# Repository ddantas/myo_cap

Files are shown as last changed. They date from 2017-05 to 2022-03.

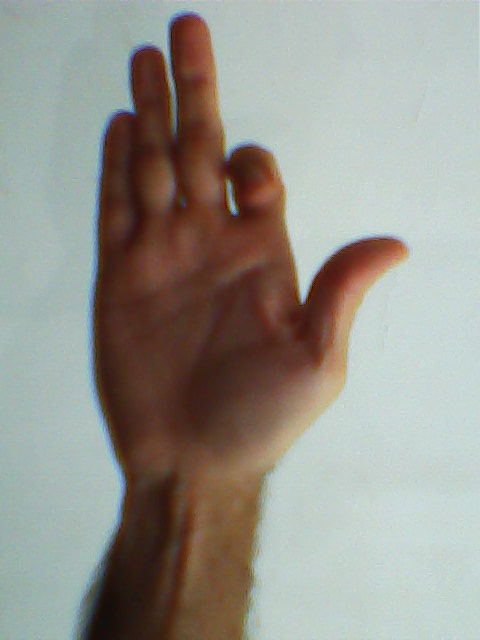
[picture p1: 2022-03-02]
software/interface/leap_cap/images/2in_curl.jpg

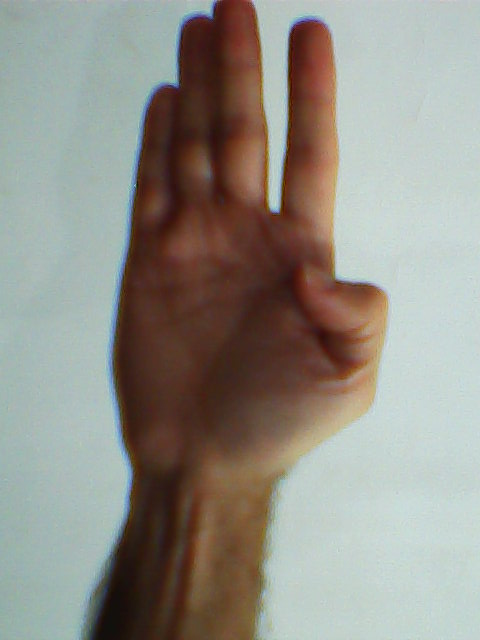
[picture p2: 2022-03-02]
software/interface/leap_cap/images/1th_curl.jpg

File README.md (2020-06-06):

# myo_cap #

## Boas práticas ##
- Antes de começar a trabalhar no código, para baixar as modificações dos outros programadores, sempre chame:
```
git pull
```

- Antes de dar commit, para ver quais arquivos foram modificados, usar:
```
git status
```

- Em seguida, apenas para os arquivos que precisam realmente ser enviados no commit, dar:
```
git add nome_do_arquivo
```

- Ao dar commit, é recomendável usar:
```
git commit -m "mensagem em inglês com o nome do commit"
```

- Depois disso, para fazer o merge com possíveis alterações recentes, dar
```
git pull
```

- E, finalmente:
```
git push
```

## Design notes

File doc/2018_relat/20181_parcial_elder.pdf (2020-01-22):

## UNIVERSIDADE FEDERAL DE SERGIPE CENTRO DE CIÊNCIAS EXATAS E TECNOLOGIA

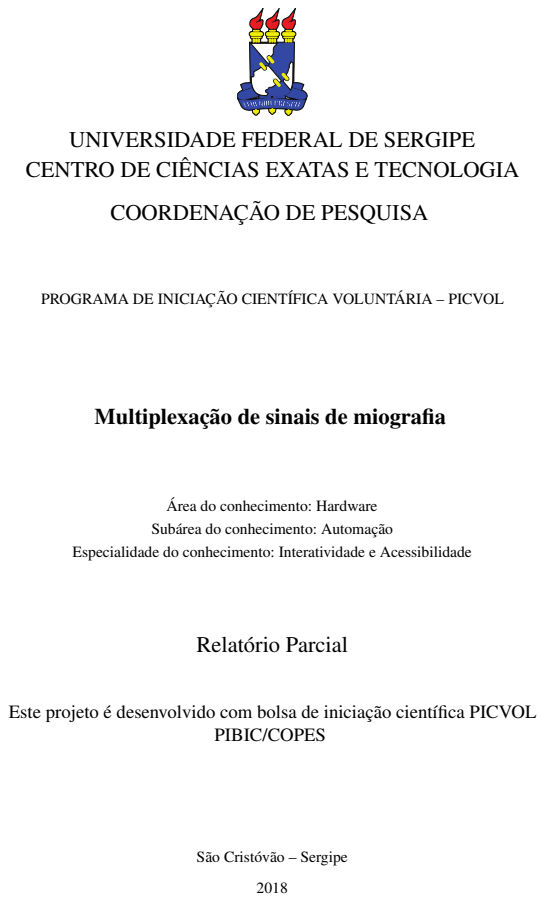
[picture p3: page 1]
Relatório Parcial; PIBIC/COPES

COORDENAÇÃO DE PESQUISA

PROGRAMA DE INICIAÇÃO CIENTÍFICA VOLUNTÁRIA – PICVOL

Multiplexação de sinais de miografia

Área do conhecimento: Hardware

Subárea do conhecimento: Automação

Especialidade do conhecimento: Interatividade e Acessibilidade

Este projeto é desenvolvido com bolsa de iniciação científica PICVOL

São Cristóvão – Sergipe

# Sumário

1

# Atividades Realizadas

Inicialmente, foi feita a revisão bibliográfica a respeito das aplicações e uso dos circuitos multiplexadores no campo dos biosinais podendo ser: eletrocardiograma, eletro-oculograma e eletromiografia.

Após a revisão bibliográfica, foi feita a pesquisa sobre qual o multiplexador atenderia aos requisitos para trabalhar com sinal mioelétrico, que possui baixa amplitude e baixa frequência.

Segundo Wang (2016), o multiplexador deve possuir baixa resistência de ligação (Ron) e baixa distorção no chaveamento dos canais, então atendendo a estes requisitos foi escolhido o multiplexador analógico CD4051.

Logo em seguida foi projetado os circuitos de multiplexação, de modo que fossem utilizados componentes de baixo custo e de fácil aquisição, comercialmente. Para isto foi utilizado o software Protheus.

Com os componentes em mãos foi feita a montagem do circuito de multiplexação para quatro canais em uma protoboard. Esse circuito tem como objetivo multiplexar os sinais obtidos de várias placas de 4 canais. Possibilitando trabalhar com um número maior de canais.

E por fim, o circuito foi testado com o auxílio do gerador de sinais e o osciloscópio, a fim de verificar a funcionalidade da comutação entre canais. Para que possa ser confeccionada a placa de circuito impresso – PCB.

2

# Justificativas de Alteração no Plano de Tra-

# balho

Não se aplica.

3

# Outras Atividades

- Participei da atividade de extensão: Seminários Sobre Internet das Coisas – IOT, com carga horária de 3 horas, coordenado pelo professor Antonio Ramirez Hidalgo, promovido pelo Departamento de Engenharia Elétrica. Onde um dos temas abortados, com relevância a esta pesquisa, foi o Monitoramento Cardíaco via Internet das Coisas. A atividade foi realizada no período de 29 a 31 de agosto de 2017;
- Participei da atividade de extensão: Electrical Day 2017, com carga horária de 8 horas, promovido pelo Empresa Júnior de Engenharia Elétrica – EPJEL, no mini curso de impressão 3D, que pode contribui no contexto geral desta pesquisa na confecção de uma mão robótica. A atividade foi realizada no dia 18 de novembro de 2017;
- Participei da atividade de extensão: IV SEMAC - minicursos Pibic 2017, com carga horária de 8 horas, coordenada pela Professora Raquel Simoes Mendes Netto, promovida pela coordenação de pesquisa, no minicurso Redação Científica e Plágio Acadêmico. A atividade foi realizada no período de 20 a 24 de novembro de 2017.
- Também foi produzido um artigo para submissão no IEEE Symposium on Computers and Communications – ISCC com qualis A2, que ocorrerá em Junho de 2018, na cidade de Natal. O título do artigo é Low cost hardware and software platform for multichannel surface electromyography. A submissão foi realizada no mês de Janeiro e em Março é esperado o resultado de aceitação.

4

# Revisão da Literatura

Eletromiografia é uma área que lida com a detecção, análise e o uso do sinal elétrico que emana das contrações musculares. Este sinal pode ser usado em diversas aplicações, desde o monitoramento dos músculos, em reabilitação de pessoas que perderam movimentos, em esportes para verificar a fadiga dos músculos e até mesmo controle de próteses biônicas (LUCA, 2006).

Amputados e indivíduos parcialmente paralisados tipicamente tem músculos intactos podendo exercer graus de liberdade variados de controle sobre estes. Além disso, existem evidências de que amputados que perderam a mão são capazes de gerar sinais nos músculos do antebraço muito semelhantes ao de uma pessoa saudável (ERIKSSON; SEBELIUS; BALKENIUS, 1998).

Para certas aplicações, como o controle de mão robótica é necessário um número maior de canais que possibilite uma quantidade maior de informações, a fim de controlar com precisão os movimentos de flexão dos dedos, do pulso ou da mão. Então é necessário multiplexar os sinais para reduzir o número de dados de saída.

Um multiplexador é um dispositivo que seleciona uma saída de muitas entradas em uma base de seleção linear e é uma parte fundamental das aplicações biomédicas (D et al., 2013).

Este plano de trabalho tem como objetivo utilizar um circuito multiplexador na etapa intermediaria entre aquisição e conversão analógico digital do sinal mioelétrico. O que permite reduzir os custos quando se deseja trabalhar com diversos canais.

5

# Metodologia

Na figura 1 é mostrado o diagrama de blocos do sistema de aquisição, multiplexação e digitalização do sinal mioelétrico. Que é composto por até 4 placas de aquisição, circuito de multiplexação, placa Tiva e um computador para visualizar os diversos sinais mioelétricos adquiridos. A etapa de multiplexação é opcional, utilizada em aplicações que necessitem de uma quantidade maior de canais.

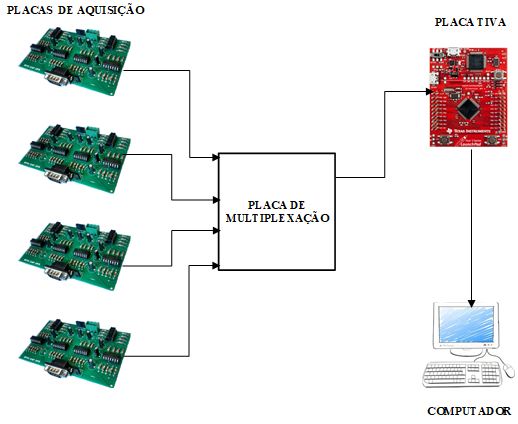
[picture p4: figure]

Figura 1 – Diagrama de blocos da plataforma.

Capítulo 5. Metodologia | 7

Na figura 2 é mostrado o diagrama esquemático da placa de multiplexação, nesse circuito é possível conectar 4 placas de aquisição de 4 canais, o total de canais que podem ser capturados com está placa são 16. A seguir é listada a nomenclatura de cada terminal:

- BOARD X – conector onde é ligado cada placa de aquisição e condicionamento do sinal mioelétrico, onde o X varia de 1 a 4;
- SELECT CHANNEL – terminais que serão ligados aos pinos da Tiva e servem para realizar a seleção de canais que serão habilitados na saída do mux;
- OUT MUX – saída dos multiplexadores que serão ligados a um circuito somador;
- TO TIVA – saída do circuito somador que será ligada a placa Tiva;
- POWER – alimentação simétrica de -9 e +9V.

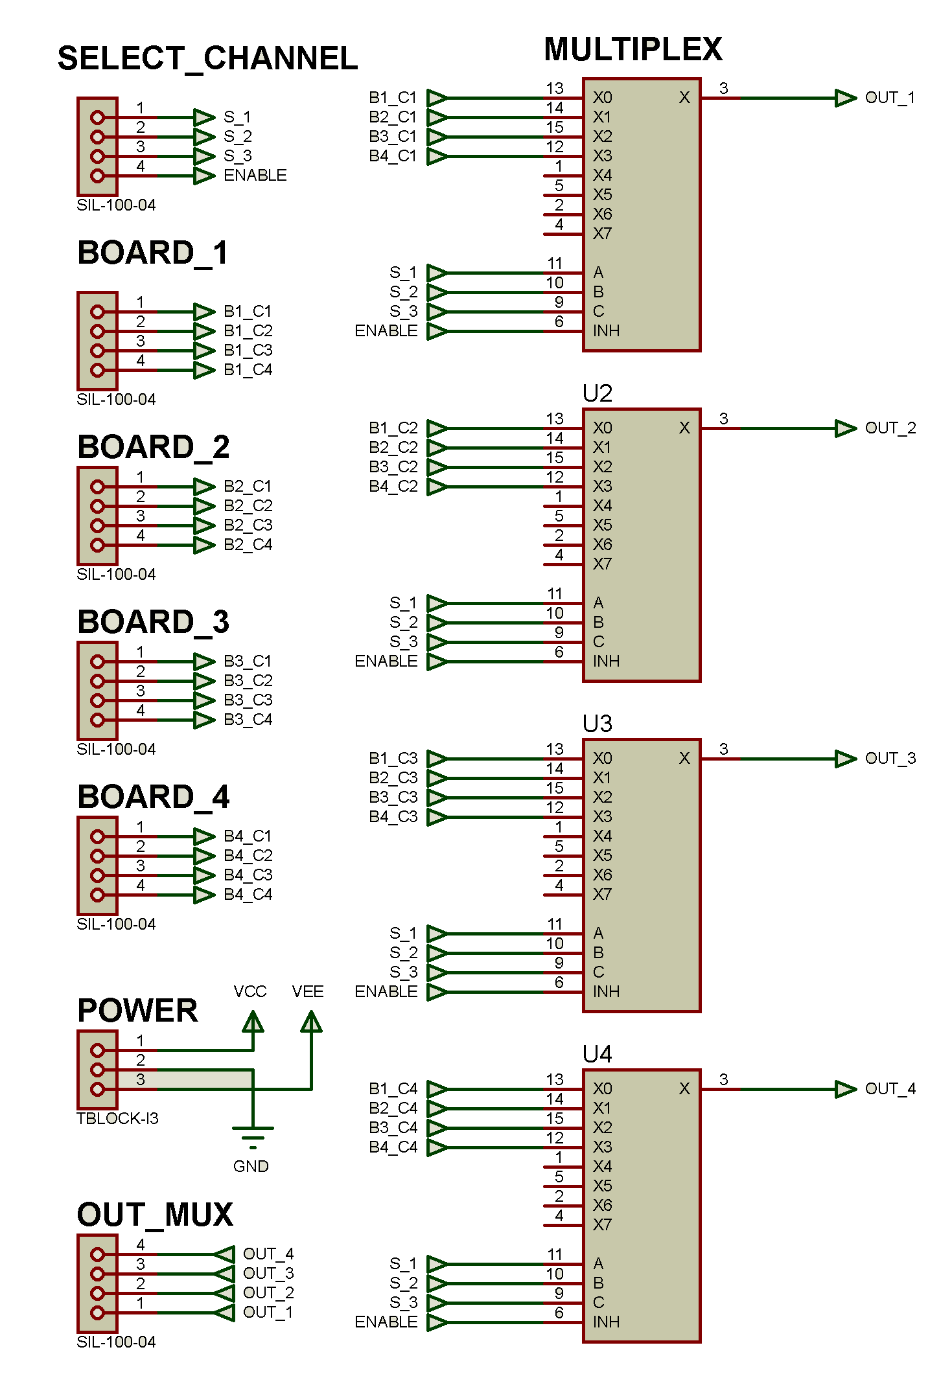
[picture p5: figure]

Figura 2 – Diagrama esquemático do circuito de multiplexação para canais.

Capítulo 5. Metodologia | 8

O multiplexador e demultiplexador analógico CD 4051 de 8 canais é um circuito integrado com tecnologia complementary metal-oxide-semiconductor – CMOS que possui 16 pinos, sendo 3 pinos de endereçamento (S1 a S3), 8 pinos independentes de entradas/saídas – I/O (Y0 a Y7) conectados a um pino comum I/O (Z). A tensão de alimentação é de 3 a 15V (VEE, VSS e VDD) e a tensão de operação é de 0 a 2 para nível logico baixo e 2.1 a 5 para nível logico alto (NEXPERIA, 2016). Na figura 3 é mostrado este circuito integrado.

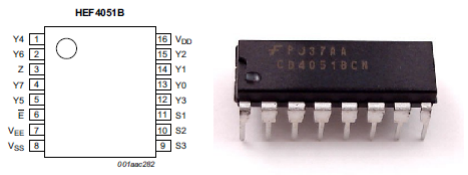
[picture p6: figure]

Figura 3 – Circuito integrado CD4051.

Neste trabalho foi utilizado a placa de desenvolvimento Tiva-C series EK-TM4C123GXL, responsável por realizar a conversão analógico-digital do sinal mioelétrico e a seleção dos canais das placas conectadas ao multiplexador a uma dada frequência de chaveamento.

É uma plataforma de baixo custo que possui microcontrolador ARM Cortex M4 de 32

bits operando a 80 MHz. Este microcontrolador é encontrados em telefones celulares, calculadoras, periféricos de computadores, equipamentos eletrônicos em geral e aplicações industriais (SOUZA, ). Na figura 4 é mostrado a placa de desenvolvimento Tiva, para programá-la pode ser usado a linguagem C com compilador fornecido pela Texas Instruments Code Composer Studio – CCS.

A placa tiva opera com valores positivos de tensão em suas entradas conectadas ao seu conversor analógico-digital, então foi necessário utilizar um circuito que eleve o nível de tensão (off-set) em 1.6V após a etapa de multiplexação, pois o sinal mioelétrico é de natureza analógica tendo valores negativos e positivos de tensão. Este circuito somador de tensão é apresentado na figura 5 abaixo.

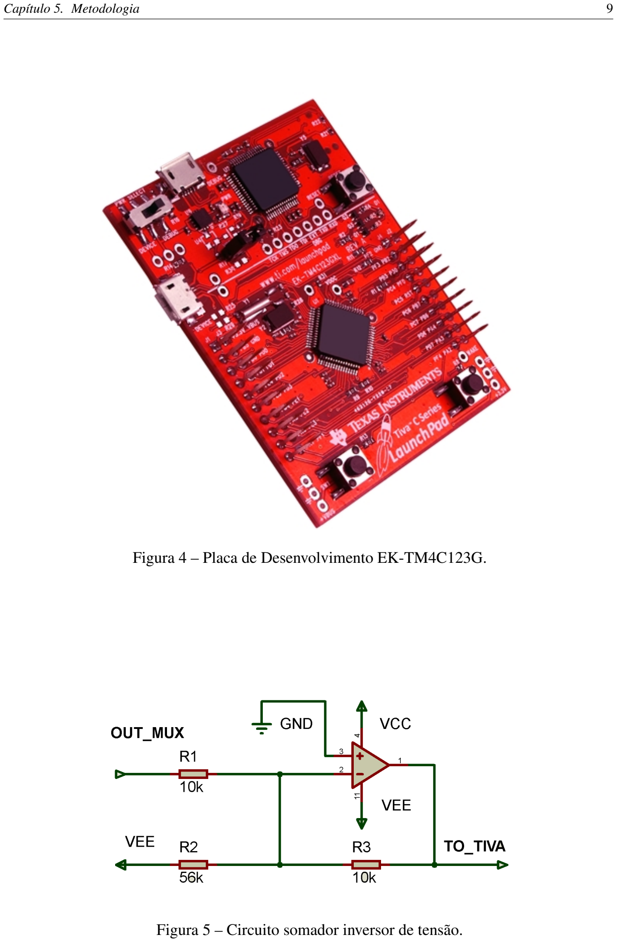
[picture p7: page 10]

Capítulo 5. Metodologia | 9

Figura 4 – Placa de Desenvolvimento EK-TM4C123G.

Figura 5 – Circuito somador inversor de tensão.

6

# Resultados preliminares

O circuito de multiplexação para quatro canais foi montado em uma protoboard em conjunto com o circuito somador e podem ser vistos na figura 6. Este circuito foi testado utilizando gerador de sinais e osciloscópio.

Foram utilizados dois sinais de entrada através do gerador de funções foi possível obter uma onda senoidal e outra onda quadrada com frequência e amplitude aproximadamente iguais como pode ser visto na figura 7

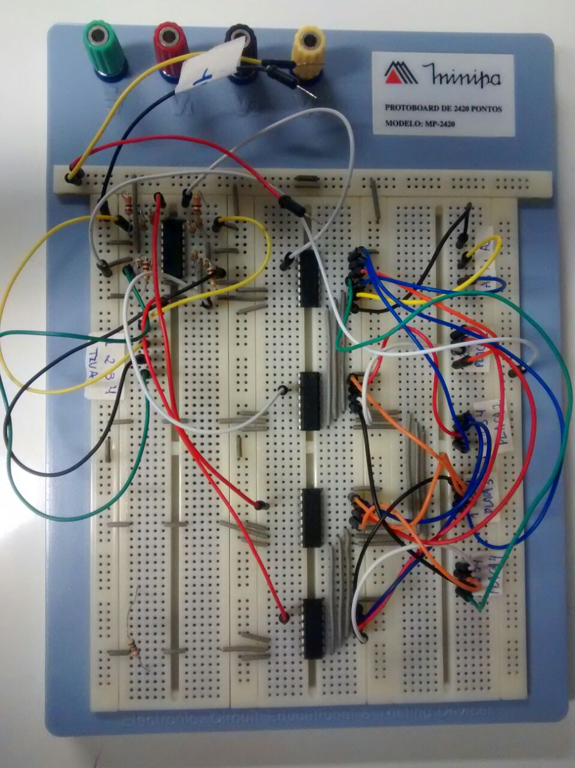
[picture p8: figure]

Figura 6 – Circuito de multiplexação montado na protoboard.

Capítulo 6. Resultados preliminares | 11

Estes sinais foram conectados a duas entradas do circuito multiplexador e a saída pode ser observada nas figuras 8 e 9. Os dois sinais de entrada simulam dois canais da placa de aquisição e na saída teremos a composição de ambos os sinais. A frequência de chaveamento e a frequência dos sinais de entrada foram variadas entre a frequência mínima e máxima do sinal mioelétrico que pela literatura é de 20 a 500Hz (LUCA, 2006).

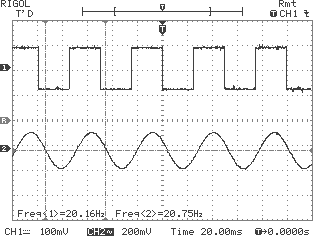
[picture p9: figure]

Figura 7 – Tela de captura do osciloscópio do sinais de entrada (onda senoidal e quadrada).

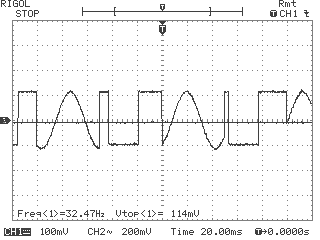
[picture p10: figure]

Figura 8 – Tela de captura do osciloscópio saída com frequência de 20Hz.

Capítulo 6. Resultados preliminares | 12

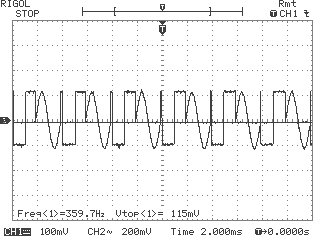
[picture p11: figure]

Figura 9 – Tela de captura do osciloscópio saída com frequência de 500Hz.

O sinal de saída é composto por um ciclos de onda quadrada e um ciclo de onda senoidal, como podem ser observados nas figuras 8 e 9. Estes sinais não sofreram distorções no chaveamento para a menor e a maior frequência do sinal aplicado.

Portanto o resultado preliminar, encontra-se dentro do esperado. Como trabalho futuro espera-se confeccionar este circuito de multiplexação em uma placa de circuito impresso e aumentar a quantidade de canais para oito.

# Referências

D, H. P. et al. Design of Ultra Low Power 8-Channel Analog Multiplexer Using Dynamic Threshold for Biosignals. [S.l.: s.n.], 2013. v. 4. DOI: 10.5121/vlsic.2013.4508.

ERIKSSON, L.; SEBELIUS, F.; BALKENIUS, C. Neural Control of a Virtual Prosthesis. In: TAYLOR, J. G. et al. (Ed.). ICANN 98. London: Springer London, 1998. p. 905–910. ISBN 978-3-540-76263-8 978-1-4471-1599-1. DOI: 10.1007/978-1-4471-1599-1_141. Disponível em: <http://link.springer.com/10.1007/978-1-4471-1599-1_141>.

LUCA, C. D. Electromyography. In: Encyclopedia of Medical Devices and Instrumentation. John Wiley & Sons, Inc., 2006. ISBN 978-0-471-73287-7. DOI: 10.1002/0471732877.emd097. Disponível em: <http://onlinelibrary.wiley.com/doi/10.1002/0471732877.emd097/abstract>.

NEXPERIA. HEF4051B 8-Channel Analog Multiplexer/Demultiplexer Datasheet. 2016. Disponível em: <https://assets.nexperia.com/documents/data-sheet/HEF4051B.pdf>.

SOUZA, S. A. Introdução aos microcontroladores ARM Cortex-M4 Tiva C Series da Texas Instruments. Disponível em: <http://www.ebah.com.br/content/ABAAAgv0gAJ/introducao-aos-microcontroladores-arm-cortex-m4-tiva-c-series-texas-instruments>. (http://www.ebah.com.br/content/ABAAAgv0gAJ/introducao-aos-microcontroladores-arm-cortex-m4-tiva-c-series-texas-instruments)

WANG, R. A Low Power 8 to 1 Analog Multiplexer for Bio-Signal Acquisition System with a Function of Amplification. Tese (Text) — Carleton University, 2016. Disponível em: <https://curve.carleton.ca/88679474-7bcd-436e-8551-e62864841f7a>.

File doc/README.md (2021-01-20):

# Link para requisitos de software #

https://www.dropbox.com/s/pmltx1t9zvk2afu/myo_cap_gui_requisitos_2021.pdf?dl=0

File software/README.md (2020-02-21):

# Funções Tivaware #

## 1.	Clock Geral do Sistema ##

### SyzCtlClockSet(uint32_t ui32Config) ###
- <b>Definição</b>: Configuração do clock geral do sistema. 
- <b>Parâmetros</b>: “ui32Config” é o parâmetro, ou os parâmetros de configuração (quando vários parâmetros, os mesmos são separados por “|”).
- <b>Exemplo</b>: 
```
SysCtlClockSet(SYSCTL_SYSDIV_5|SYSCTL_USE_PLL|SYSCTL_XTAL_16MHZ|SYSCTL_OSC_MAIN);
```
No exemplo acima, pode ser verificado a utilização de um cristal externo de 16MHz, representados pelos parâmetros SYSCTL_XTAL_16MHZ e SYSCTL_OSC_MAIN e configuração do clock do sistema através de uma PLL (que possui 200MHz de referencia para cálculos) e divisão da mesma por 5, representadas pelos parâmetros SYSCTL_SYSDIV5 e SYSCTL_USE_PLL. 
Assim, o clock geral do sistema estará configurado para trabalhar com o cristal de 16 MHz da placa de desenvolvimento e estará funcionando a 40 MHz conforme a divisão da PLL escolhida.

### SysCtlPeripheralEnable(ui32Peripheral) ###
- <b>Definição</b>: Função para habilitar periférico, como o GPIO.
- <b>Parâmetros</b>: “ui32Peripheral” é o periférico a ser habilitado.
- <b>Exemplo</b>: 
```
SysCtlPeripheralEnable(SYSCTL_PERIPH_GPIOF);
```
Habilitação do periférico GPIO Port F.

## 2.	Configurando e usando o GPIO ##
### GPIOPinTypeGPIOOutput(uint32_t ui32Port, uint8_t ui8Pins) ###
- <b>Definição:</b> Função onde um pino da GPIO é configurado como saída.
- <b>Parâmetros:</b> “ui32Port” representa o PORT a ser configurado e o “ui8Pins” o pino.

### GPIOPinTypeGPIOInput(uint32_t ui32Port, uint8_t ui8Pins) ###
- <b>Definição:</b> Função onde um pino da GPIO é configurado como entrada.
- <b>Parâmetros:</b> “ui32Port” representa o PORT a ser configurado e o “ui8Pins” o pino.
- <b>Exemplo</b>:
```
  SysCtlPeripheralEnable(SYSCTL_PERIPH_GPIOF); 
  GPIOPinTypeGPIOOutput(GPIO_PORTF_BASE, GPIO_PIN_1|GPIO_PIN_2|GPIO_PIN_3);
  GPIOPinTypeGPIOInput(GPIO_PORTF_BASE, GPIO_PIN_4|GPIO_PIN_0);
```
O exemplo acima configura na PORT F, os pinos PF1, PF2 e PF3 como saída (LED RGB da Launchpad) e os pinos PF0 e PF4 como entrada (dois botões da Launchpad). 

### GPIOPinRead(uint32_t ui32Port, uint8_t ui8Pins) ###
- <b>Definição:</b> Função que retorna se o pino está em nível lógico alto ou baixo.
- <b>Parâmetros: </b> “ui32Port” representa o PORT e o “ui8Pins” o pino a serem lidos.
- <b>Exemplo:</b> 
```
GPIOPinRead(GPIO_PORTF_BASE, GPIO_PIN_4);
```
Retorna o endereço, ou valor, do PIN_4 do PORTF caso 1.

### GPIOPinWrite(uint32_t ui32Port, uint8_t ui8Pins, uint8_t ui8Val) ###
- <b>Definição:</b> Função que manda o nível lógico alto ou baixo para o pino em questão.
- <b>Parâmetros:</b> “ui32Port” representa o PORT, o “ui8Pins” o pino de entrada e “ui8Val” o valor.
- <b>Exemplo:</b> 
```
GPIOPinWrite(GPIO_PORTF_BASE,GPIO_PIN_1|GPIO_PIN_2|GPIO_PIN_3,GPIO_PIN _2); 
```
Aciona somente o PIN_2 do PORTF

## 3.	Utilizando uma UART ##

### UARTConfigSetExpClk(uint32_t ui32Base, uint32t ui32UARTClk, uint32_t ui32Baud, uint32_t ui32Config) ###
- <b>Definição:</b> Função que configura os parâmetros da serial utilizada.
- <b>Parâmetros:</b> “ui32Base” é a UART port ,  “ui32UARTClk” é o clock disponível para o modulo UART, “ui32Baud” é o baud rate, “ui32Config” indica o formato dos dados.

### UARTCharPut(uint32_t ui32Base, unsigned char ucData) ###
- <b>Definição: </b> Função que imprime na serial o parâmetro ucData.
- <b>Parâmetros: </b> “ui32Base” é a UART port, “ucData” é o caractere a ser transmitido.

### UARTPrintf(unsigned char *ucData) ###
- <b>Definição: </b> Função que imprime na serial o parâmetro ucData.
- <b>Parâmetros: </b> “ucData” é o caractere a ser transmitido.

### UARTCharGet(uint32_t ui32Base) ###
- <b>Definição:</b> Função que retorna o caractere lido na serial como int32_t.
- <b>Parâmetros:</b> “ui32Base” é a UART port.
- <b>Exemplo:</b> 
```
void ConfigureUART(void) { 
  SysCtlPeripheralEnable(SYSCTL_PERIPH_GPIOA);
  SysCtlPeripheralEnable(SYSCTL_PERIPH_UART0);
  GPIOPinConfigure(GPIO_PA0_U0RX); 
  GPIOPinConfigure(GPIO_PA1_U0TX); 
  GPIOPinTypeUART(GPIO_PORTA_BASE, GPIO_PIN_0 | GPIO_PIN_1);
  UARTClockSourceSet(UART0_BASE, UART_CLOCK_PIOSC); 
  UARTStdioConfig(0, 115200, 16000000); 
}
```

## 4.	Configurando interrupções. ##
### Configurando o ambiente ###
- <b>1º Passo:</b> Declare a função a ser chamada através da interrupção desejada como função externa ao código, aproximadamente na linha 58 do código do “tm4c123gh6pmi_sturtup_ccs.c”.
- <b>2º Passo:</b> Adicione essa função ao vetor de interrupções em sua devida posição substituindo a função padrão “IntDefaultHandler” pela sua função utilizada. Para uma interrupção no PORTF, sua posição será aproximadamente na linha 116 do código do “tm4c123gh6pmi_startup_ccs.c”. Após estas configurações, sempre que houver uma borda de descida no pino 4 do PortF (SW1 pressionado), sua função de interrupção será executada!

### IntMasterEnable() ###
- <b>Definição:</b> Função que permite ao processador responder a todas as chamadas de interrupção utilizadas.

### GPIOIntEnable(uint32_t ui32Port, uint32_t ui32IntFlags) ###
- <b>Definição:</b> Função onde um pino da GPIO do microcontrolador é configurado como interrupção e o parâmetro ui32IntFlags representa o pino a ser configurado da seguinte forma: GPIO_INT_PIN_0, GPIO_INT_PIN_1, ... ou GPIO_INT_PIN_7.
- <b>Parâmetros:</b> “ui32Port” é o GPIO port, “ui32IntFlags” é o pino do GPIO port.

### GPIOIntTypeSet(uint32_t ui32Port, uint8_t ui8Pins, uint32_t ui32IntType) ###
- <b>Definição:</b> Função onde um pino da GPIO do microcontrolador que é configurado como interrupção tem o seu modo de habilitação configurado, e o parâmetro ui32IntType que representa o modo de habilitação da interrupção pode ser configurado como: GPIO_FALLING_EDGE (para borda de descida), GPIO_RISING_EDGE (para borda de subida), GPIO_BOTH_EDGE (qualquer borda), GPIO_LOW_LEVEL (nível lógico baixo) e GPIO_HIGH_LEVEL (nível lógico alto).
- <b>Parâmetros:</b> “ui32Port” é o GPIO port, “ui8Pins” são os pinos, “ui32IntType” representa o modo de habilitação da interrupção.

## 5.	Configurando o Timer ##

### Configurando o ambiente ###
- <b>1º Passo:</b> Declare a função a ser chamada através da interrupção desejada como função externa ao código, aproximadamente na linha 59 do código do “tm4c123gh6pmi_sturtup_ccs.c”.
- <b>2º Passo:</b> Adicione essa função ao vetor de interrupções em sua devida posição substituindo a função padrão “IntDefaultHandler” pela sua função utilizada. Para uma interrupção no PORTF, sua posição será aproximadamente na linha 106 do código do “tm4c123gh6pmi_sturtup_ccs.c”.Após estas configurações, sempre que o timer atingir o período de contagem selecionado, ele vai gerar uma interrupção e a função declarada será executada!

### TimerConfigure(uint32_t ui32Base, uint32t ui32Config) ###
- <b>Definição:</b> Função que configura o tipo de timer utilizado onde o parâmetro ui32Config e escolhido conforme a configuração de Timer periódico, Disparo único, PWM, etc.  
- <b>Parâmetros:</b> "ui32Base" é o endereço base para o modulo do timer, "ui32Config" tipo de configuração do timer (Periódico, disparo único, PWM).

### TimerEnable(uint32_t ui32Base, uint32_t ui32Timer) ###
- <b>Definição:</b> Função que habilita o timer escolhido após a sua configuração onde o parâmetro ui32Timer é o Timer escolhido: TIMER_A, TIMER_B, ou TIMER_BOTH.
- <b>Parâmetros:</b> "ui32Base" é o endereço base para o modulo do timer, "ui32Timer" é o timer escolhido.

### TimerLoadSet(uint32_t ui32Base, uint32_t ui32Timer, uint32_t ui32Value) ###
- <b>Definição: </b> Função que seleciona o valor de estouro do Timer (Em caso de Timer periódico) onde o parâmetro ui32Value é um número inteiro representado por até 32 bits.
- <b>Parâmetros: </b> "ui32Base" é o endereço base para o modulo do timer, "ui32Timer" é o timer escolhido, "ui32Value" é o clock geral dividido pela frequencia gerada (ClockGeral / ClockDesejado).  

### TimerIntClear(uint32_t ui32Base, uint32_t ui32IntFlags) ###
- <b>Definição:</b> Função que deve ser chamada após a interrupção do timer periódico para manter o Trigger.
- <b>Parâmetros:</b> "ui32Base" é o endereço base para o modulo do timer, "ui32IntFlags" mascara de bits utilizada para limpar o vetor de interrupções do timer em questão.

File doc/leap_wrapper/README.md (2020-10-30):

# Leap Motion SDK 2.3.1 setup to python 3.7 #

Download the files:
- LeapDeveloperKit_2.3.1+31549_linux.tgz (at https://drive.google.com/file/d/1hoI6lLrYuk5U4TdiEWrbKYNq9NrEPoBq/view?usp=sharing)
- LeapDeveloperKit_linux-hotfix_2.3.1+33747_linux.tgz (at https://drive.google.com/file/d/1m9wo-nC4tkubOtHWYDED7r9XGPjnPyqr/view?usp=sharing)
- Leap.i.diff

## 1. Dependencies ##

- Install the packages:

```
sudo apt-get install libgl1-mesa-dri libgl1-mesa-glx
sudo apt-get install swig g++ libpython3.7-dev
```

## 2. Installation ##

- Extract files:

```
tar -xaf LeapDeveloperKit*31549*.tgz
tar -xaf LeapDeveloperKit*33747*.tgz
```

- Install client software:

``` 
cd LeapDeveloperKit*33747*
sudo dpkg -i Leap*x64.deb
sudo leapd
```

- If you don't have the file /etc/init.d/leapd, create it:

```
sudo nano /lib/systemd/system/leapd.service
```

- Put the following code in the file leapd.service:

```
[Unit]
Description=LeapMotion Daemon
After=syslog.target

[Service]
Type=simple
ExecStart=/usr/sbin/leapd

[Install]
WantedBy=multi-user.target
```

- Then:
```
sudo ln -s /lib/systemd/system/leapd.service /etc/systemd/system/leapd.service
sudo systemctl daemon-reload or sudo service leapd restart
```

-  Create Leap Motion wrapper

```
cd ../LeapDeveloperKit*31549*/LeapSDK
mkdir python3.7_project
cp -a lib/x64/libLeap.so lib/Leap.py samples/Sample.py python3.7_project/
2to3-3.7 -nw python3.7_project/Sample.py
patch -p0 < Leap.i.diff
swig -c++ -python -o /tmp/LeapPython.cpp -interface LeapPython include/Leap.i
g++ -fPIC -I/usr/include/python3.7m -I./include /tmp/LeapPython.cpp lib/x64/libLeap.so -shared -o python3.7_project/LeapPython.so
cd python3.7_project/
LD_PRELOAD=./libLeap.so python3.7 Sample.py
```
# Leap Motion SDK 2.3.1 for Windows #

Download the file:
- Leap_Motion_SDK_Windows_2.3.1 (https://drive.google.com/file/d/1y5BmwmOZeAhrRCbbuTK28OVA80gQvlsQ/view?usp=sharing)

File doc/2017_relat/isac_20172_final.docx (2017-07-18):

UNIVERSIDADE FEDERAL DE SERGIPE

CENTRO DE CIÊNCIAS EXATAS E TECNOLÓGICAS

DEPARTAMENTO DE COMPUTAÇÃO

Isac Alencar Rodrigues da Silva

Aquisição de sinais de miografia através de circuitos de baixo custo

São Cristóvão

2017

Isac Alencar Rodrigues da Silva

Aquisição de sinais de miografia através de circuitos de baixo custo

Relatório final destinado à COPES/UFS referente ao Programa Institucional de Bolsas de Iniciação Científica (PIBIC).

Orientador: Prof. Dr. Daniel Oliveira Dantas.

São Cristóvão

2017

RESUMO

A eletromiografia (EMG) é a disciplina que lida com a detecção, a análise e o uso do sinal elétrico que emana da contração de um músculo, também conhecido como sinal mioelétrico [1]. Uma das formas de adquirir esse sinal é através de eletrodos de superfície, posicionados sobre a pele de uma determinada região de interesse. Desta forma, este projeto de iniciação científica tem a finalidade de desenvolver um sistema aquisição, condicionamento e transferência de sinais mioelétricos para um computador, para que sejam usados, por exemplo, no controle de uma mão robótica.

Palavras-chave: eletromiografia, sinal mioelétrico, eletrodo, superfície, aquisição.

SUMÁRIO

1 INTRODUÇÃO | 04
1.1 OBJETIVOS | 05
2 FUNDAMENTAÇÃO TEÓRICA | 06
2.1 CARACTERÍSTICAS DO SINAL MIOELÉTRICO E SUA AQUISIÇÃO | 06
2.2 AMPLIFICADOR DE INSTRUMENTAÇÃO | 08
2.3 FILTROS ATIVOS | 10
2.4 CONVERSÃO ANALÓGICO-DIGITAL | 11
3 DESENVOLVIMENTO | 13
3.1 PROJETO DO CIRCUITO DE AQUISIÇÃO E CONDICIONAMENTO | 13
3.2 TESTES COM PLACA DE CIRCUITO IMPRESSO | 15
3.3 CIRCUITO DE AQUISIÇÃO E CONDICIONAMENTO PARA 4 CANAIS | 18
3.4 TESTES COM PLACA DE CIRCUITO IMPRESSO PARA 4 CANAIS | 19
4 CONCLUSÃO | 24
REFERÊNCIAS BIBLIOGRÁFICAS | 25

1 INTRODUÇÃO

O corpo humano pode ser considerado uma “máquina” perfeita, no sentido de que todas as suas partes trabalham em harmonia umas com as outras. A maioria das pessoas controla essa máquina naturalmente no seu dia a dia, exceto quando um distúrbio é provocado, devido a doenças ou lesões que resultem na perda de funcionalidades do corpo.

A ausência de membros é um exemplo de distúrbio que modifica profundamente a vida de uma pessoa, pois tarefas simples como caminhar e segurar objetos com as mãos podem tornar-se extremamente difíceis ou impossíveis de serem executadas. Por isso, uma das soluções adotadas para restabelecer parte desse tipo funcionalidade perdida é o uso de membros artificiais.

Desde a criação dos primeiros membros artificiais, um dos grandes desafios dos pesquisadores tem sido o aperfeiçoamento destas ferramentas, a fim de que possam ser controladas da maneira mais natural possível pelos pacientes [2] [3] [4]. O controle atual dessas próteses baseia-se principalmente na análise de duas classes de fontes de sinais: biomecânica e bioelétrica. Na biomecânica são considerados estudos sobre o movimento de partes do corpo, as alterações nas propriedades de um componente do corpo como resultado de uma atividade mecânica e o controle do fluxo de ar. Já na bioelétrica são analisados sinais elétricos resultantes de atividades cerebrais, neurais, oculares e musculares – que são os sinais de interesse para este trabalho.

O estudo da dinâmica muscular baseia-se num princípio estabelecido há mais de 200 anos por Galvani [4], segundo o qual um músculo esquelético estimulado eletricamente se contrai e, por outro lado, produz corrente elétrica quando se contrai voluntariamente. Essa ideia também é o principal fundamento da Eletromiografia, disciplina que lida com a detecção, a análise e o uso do sinal elétrico que emana da contração muscular, também chamado de sinal miolelétrico.

A Eletromiografia de Superfície possibilita a aquisição desse sinal sem procedimentos invasivos, utilizando eletrodos sobre a pele – conhecidos como eletrodos de superfície [1] – na região de interesse. Porém, uma das desvantagens desse método é a presença de uma quantidade maior de ruído do que nos métodos invasivos, distorcendo o sinal mioelétrico, já que ele não é adquirido diretamente do músculo.

Para lidar com esse tipo de problema é necessário utilizar amplificadores e filtros adequados nas etapas de aquisição e condicionamento do sinal. Portanto, este trabalho buscará: desenvolver um sistema de captura de sinais mioelétricos gerados pelos músculos do antebraço a partir de eletrodos de superfície, digitalizá-los e transmiti-los para um computador. Uma vez armazenadas, estas informações poderão ser utilizadas, por exemplo, para o controle de uma mão robótica.

1.1 OBJETIVOS

O objetivo principal deste trabalho é implementar um conjunto de hardware e software, de baixo custo, que realizará a aquisição e o condicionamento de múltiplos sinais mioelétricos simultaneamente.

De forma específica, o projeto também buscará:

- Minimizar artefatos e ruído na etapa de aquisição do sinal de interesse;
- Aplicar filtros analógicos que condicionem o sinal à faixa de frequência desejada;
- Digitalizar o sinal e enviá-lo para um computador, preferencialmente via porta USB;
- Realizar os passos anteriores para múltiplas capturas de sinais mioelétricos, simultaneamente, ou seja, para múltiplos canais.

2 FUNDAMENTAÇÃO TEÓRICA

Neste capítulo será apresentada a fundamentação teórica necessária para o entendimento básico das características do sinal mioelétrico, assim como os princípios do circuito elétrico responsável pela aquisição e pelo seu condicionamento.

2.1 CARACTERÍSTICAS DO SINAL MIOELÉTRICO E SUA AQUISIÇÃO

Os músculos esqueléticos são formados por fibras musculares que são organizadas em feixes, compostos por fios finos de duas moléculas de proteínas (actina e miosina). Quando um potencial de ação é disparado pelo nervo motor associado a um grupo de fibras musculares ocorre o processo de contração muscular, provocando o deslocamento das fibras de actina e miosina (figura 1). A soma desses potenciais gerados pelas fibras musculares, quando elas são excitadas por neurônios motores, compõe o sinal mioelétrico. Desta forma, ele é a manifestação de uma ativação neuromuscular associada a uma contração muscular.

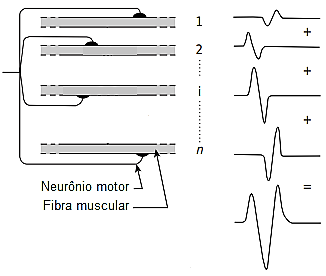
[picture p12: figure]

Figura 1. Representação da geração do potencial de ação de uma unidade motora, que é formado pelo potencial individual das fibras musculares.

Um exemplo de sinal mioelétrico pode ser visto na figura 2. Nele, o sinal inicia com uma baixa amplitude que, quando expandida, revela os potenciais de ação individuais associados à atividade contrátil de fibras musculares (individuais ou um pequeno grupo). À medida que a força resultante da contração muscular aumenta, mais fibras deslocam-se e a taxa de ativação delas também aumenta. De maneira correspondente, a amplitude do sinal cresce assumindo a forma e as características de uma variável de distribuição Gaussiana [1].

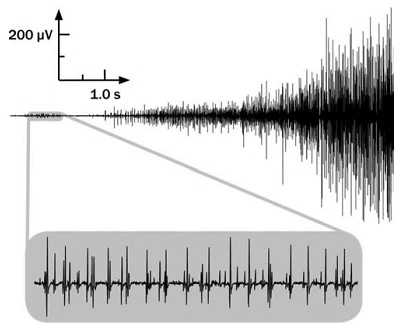
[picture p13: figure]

Figura 2. Sinal mioelétrico capturado a partir de eletrodos sobre a pele. O sinal cresce em amplitude à medida que a força produzida por um músculo aumenta.

Uma das formas para se adquirir sinais mioelétricos, como o da figura 2, é através de eletrodos de superfície. Sua função é converter a corrente iônica bioelétrica em uma corrente formada por elétrons. Os materiais mais utilizados para sua composição são Prata/Cloreto de Prata (Ag/AgCl) e Prata (Ag) [6]. Sua principal vantagem é a facilidade e padronização na aplicação, por ser uma técnica não invasiva. Porém, apresenta limitações como: a atenuação causada pelo tecido subcutâneo, a possível contaminação do registro por atividade elétrica oriunda de outros músculos ou grupos musculares - conhecida na literatura por croostalk [1] - e interferências eletromagnéticas, provenientes do movimento dos cabos e da proximidade de equipamentos eletrônicos e da rede elétrica.

Para o registro da atividade muscular pode-se utilizar uma configuração bipolar, em que dois eletrodos são colocados sobre o músculo de interesse e o potencial entre eles é registrado em relação a uma referência - geralmente um eletrodo localizado em outra parte do corpo, não relacionada à parte com que se está trabalhando. A partir dessa configuração é possível minimizar o ruído comum aos sinais adquiridos pelos eletrodos de detecção através de um amplificador diferencial. A figura 3 apresenta um esquema desse arranjo.

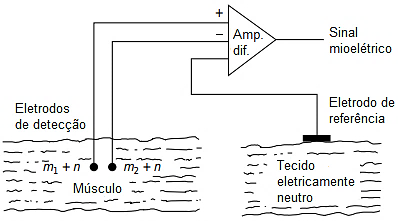
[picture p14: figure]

Figura 3. Detecção com arranjo bipolar. Neste tipo de configuração os sinais mioelétricos são considerados diferentes (m1 e m2), enquanto o ruído é similar (n).

Existem também outras duas características importantes acerca dos sinais adquiridos na Eletromiografia de Superfície. A primeira delas diz respeito à amplitude do sinal. Sua faixa típica está entre 0 e 10mV (pico a pico) [7] e deve ser considerada no projeto de ganho do circuito de aquisição. A outra característica fundamental refere-se à largura de banda do sinal, que encontra-se no intervalo de 0 a 500Hz [7], e pode ser utilizada na definição dos parâmetros do circuito de condicionamento.

2.2 AMPLIFICADOR DE INSTRUMENTAÇÃO

Os amplificadores operacionais (amp-ops) são o bloco básico da Eletrônica Analógica [8]. O amp-op clássico é chamado de amplificador diferencial, já que amplifica a diferença entre dois sinais em suas duas entradas. Porém, é um circuito construído de tal forma que suas características de operação podem ser alteradas pelo tipo e intensidade de realimentação que ele recebe.

Como mostra a figura 4, o amplificador operacional possui duas entradas, uma inversora (V–) e outra não-inversora (V+), e um terminal de saída (Vout) referenciado ao mesmo ponto comum (terra) das duas fontes de tensão simétricas que o alimentam (+Vcc e –Vcc). Na figura 5 é apresentado um modelo mais detalhado de um amp-op: ganho de tensão (A), impedância de entrada (Zin), resposta de frequência e taxa de rejeição para sinais em modo comum infinitos; e também impedância de saída (Zout) nula [8]. A taxa de rejeição em modo-comum (CMRR – Common-Mode Rejection Rate) é a medida da habilidade do amp-op em rejeitar sinais que são comuns a ambas as entradas, como ruídos e interferências eletromagnéticas.

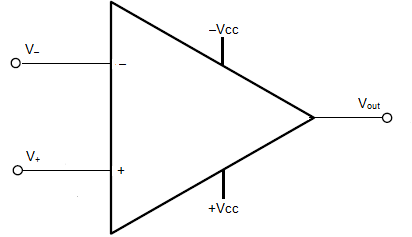
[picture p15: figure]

Figura 4. Representação de um amplificador operacional (amp-op), em que suas entradas são V– e V+, suas tensões de alimentação simétrica são +Vcc e –Vcc e sua saída Vout.

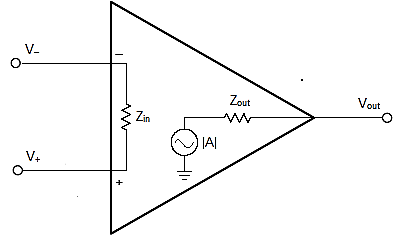
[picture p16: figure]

Figura 5. Representação detalhada de um amp-op, em que |A|=(V_(out))/((V_(+) -V_(-) )) .

Um amplificador operacional real, em loop aberto, não tem qualquer aplicação prática. Nessa configuração, seu elevadíssimo ganho de tensão faz com que ele fique muito sensível, a ponto de que, mesmo sem qualquer sinal aplicado às suas entradas, o amp-op fique instável e sua saída sature ora em uma tensão de alimentação simétrica ora em outra, sem qualquer controle [8]. Portanto, em muitas aplicações utiliza-se a realimentação negativa para solucionar este problema, assim como a associação de amplificadores e outros componentes, a fim de aproximar-se das característica de um amplificador ideal.

A configuração do amplificador de instrumentação, utilizada para registrar a diferença entre duas tensões, é capaz de atingir elevados CMRR e impedância de entrada e pequenos ganhos [8]. Isso é feito utilizando-se três amplificadores, dois com a função de buffer – que é um repetidor de tensão – nas entradas e um com a função de subtrair tensões e amplificar essa diferença, como apresenta a figura 6. Devido a essas características, o amplificador de instrumentação é comumente usado na aquisição de sinais biomédicos. Sua equação de saída é dada pela equação 1:

| V_(out) =(V_2 -V_1 )*(1+(2*R2)/(R1))*((R4)/(R3)) | (1)

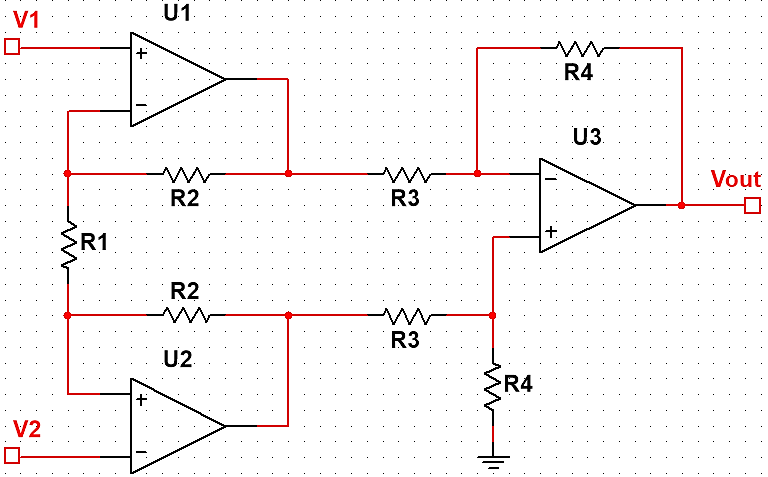
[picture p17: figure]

Figura 6. Esquema do circuito elétrico de um amplificador de instrumentação, com tensão de saída fornecida pela equação 1.

2.3 FILTROS ATIVOS

Na Eletrônica, um filtro é um circuito que aceita em sua entrada sinais elétricos de amplo espectro de frequência e apresenta na saída esses sinais atenuados, quando os mesmos encontram-se fora de uma faixa de frequência selecionada. De acordo com esse intervalo de frequência os filtros podem ser classificados em: passa-baixas, passa-altas, passa-faixa e rejeita-faixa [9].

Os filtros passa-baixas (LPF – Low Pass Filter) são aqueles que deixam “passar” somente os sinais que estejam abaixo de uma determinada frequência, chamada frequência de corte, e bloqueiam todas as outras acima dessa. Os filtros passa-altas (HPF – High Pass Filter) permitem a passagem de sinais com frequências acima da de corte. Os passa-faixa (BPF – Band Pass Filter) são aquelas que possuem frequências de corte inferior e superior, permitindo a passagem de sinais dentro do intervalo definido por essas duas frequências. Por fim, os filtros rejeita-faixa (BRF – Band Reject Filter) bloqueiam todos os sinais dentro de duas frequências de corte e permitem a passagem de todas as outras.

Os filtros em Eletrônica ainda podem ser do tipo passivo – quando são construídos com resistores e capacitores – ou ativo – quando também utilizam transistores e circuitos integrados, como os amp-ops [9]. A amplitude do sinal registrado na saída de um filtro passivo é sempre atenuada por seus componentes e pode ainda ter sua resposta em frequência alterada pela impedância do circuito a ele conectado. Nas aplicações em que se deseja minimizar tais problemas os filtros ativos são utilizados, já que, por exemplo, os amplificadores operacionais presentes nesses filtros podem ter elevada impedância de entrada e o ganho de tensão é controlado.

2.4 CONVERSOR ANALÓGICO-DIGITAL

Com o intuito de transmitir, processar, armazenar e exibir informações de sinais de natureza analógica na forma digital, uma conversão analógica para digital precisa ser feita. Este processo é realizado por um dispositivo chamado conversor analógico-digital (ADC, analog to digital converter) [10].

Há diversos tipos de conversores AD, que usam diferentes modos para se obter um equivalente discreto do sinal contínuo. Porém, todos eles compartilham as seguintes características e limites:

- Taxa de amostragem: a taxa em que cada valor discreto – que representa o sinal contínuo – é amostrado é chamada taxa de amostragem ou frequência de amostragem. Este parâmetro expressa quantos valores são criados em um dado período por um ADC.

A taxa de amostragem deve ser selecionada levando-se em conta o cumprimento do Teorema da Amostragem de Nyquist-Shanon. Resumidamente, ele afirma que a frequência de amostragem precisa ser, no mínimo, duas vezes maior que a frequência mais alta amostrada. Se o teorema não for respeitado, o fenômeno de aliasing ocorre.

- Aliasing: o efeito aliasing faz com que as versões discretas de dois sinais contínuos distintos não possam ser diferenciadas. Quando isto acontece, o sinal original não pode mais ser reconstruído a partir do seu discreto equivalente, causando perda de informação.

Entre duas amostras consecutivas, existe um “vazio de informação” porque é impossível saber os valores assumidos pelo sinal analógico. Se o sinal for lento, é plausível supor que os valores analógicos existentes em um intervalo de amostragem são semelhantes as amostras anterior e atual. No entanto, se o sinal é muito rápido em relação à taxa de amostragem, diversos valores distintos podem se perder entre o intervalo de duas amostras. A figura 7 ilustra um exemplo do efeito aliasing.

- Resolução: a resolução de um ADC é o número de valores discretos que ele pode produzir ao longo da gama de valores de entrada analógicos. Quanto maior a resolução, maior a precisão das medidas tomadas pelo ADC.

Um ADC de n bits possui 2^n níveis discretos distintos para representar um sinal analógico e, portanto, um valor elevado de n significa um ADC com maior precisão. Por exemplo, um ADC de 8 bits é capaz de produzir 256 níveis discretos, enquanto um de 12 bits produz 4096 níveis. Para uma entrada com escala de amplitude de 0 a 10V, o ADC de 8 bits mapeará diferenças de tensão de cerca de 39mV para um mesmo nível discreto. Enquanto isso, um ADC de 12 bits será capaz de mapear em níveis distintos as diferenças de tensão de cerca de 2.4mV.

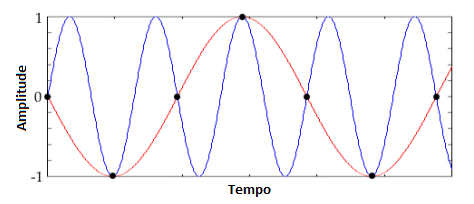
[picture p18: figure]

Figura 7. O sinal de alta frequência (azul) foi amostrado com uma taxa abaixo da que é pedida pelo Teorema da Amostragem. Assim, não é possível inferir se a representação digital (pontos pretos) é proveniente do sinal de alta frequência ou de um sinal de baixa frequência (vermelho).

3 DESENVOLVIMENTO

Neste capítulo serão apresentadas as etapas do trabalho desenvolvidas, assim como os resultados parciais obtidos. Essas etapas incluem: o projeto de circuitos para aquisição e condicionamento de sinais mioelétricos, utilizando-se uma configuração bipolar de eletrodos, e a confecção e o teste de placas de circuito impresso para estes projetos.

3.1 PROJETO DO CIRCUITO DE AQUISIÇÃO E CONDICIONAMENTO

Na figura 7 é apresentado o esquema do circuito de aquisição do sinal mioelétrico. Basicamente, ele é composto por um amplificador de instrumentação (figura 6), ao qual foi adicionado um circuito de referência, responsável por atenuar o ruído de modo comum presente nos eletrodos. Os eletrodos que fornecem a saída diferencial TO_FILTER_1 são conectados aos terminais IN1 e IN2, enquanto o eletrodo de referência é conectado ao terminal REF_ELETRODE. Seu ganho G1, obtido a partir da equação 1, é dado por:

| G_1 =(1+(2*R2)/(R1))*((R4)/(R3)), | (2)

A partir dos valores dos componentes apresentado na figura 7, o ganho G1 da equação 2 é aproximadamente igual a 7,3.

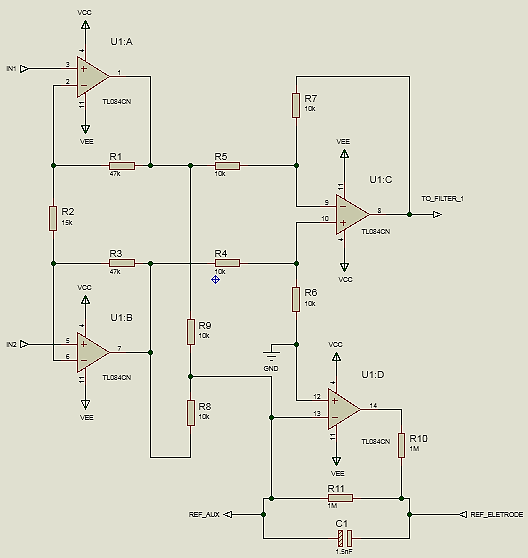
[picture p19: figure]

Figura 7. Circuito de aquisição do sinal mioelétrico a partir da configuração bipolar de eletrodos. Os eletrodos conectados aos terminais V1 e V2 fornecem a saída diferencial Vout1 e o eletrodo de referência é conectado ao terminal Vref.

O circuito de condicionamento é composto por dois filtros ativos, primeiro um passa-altas e, em seguida, um passa-baixas, como mostra a figura 8. As frequências de corte dos filtros passa-altas (fc1) e passa-baixas (fc2) são dadas pelas equações 3 e 4. O filtro passa-altas também aplica um ganho (G2) à sua entrada, que é dado pela equação 5.

| f_(c1) =1/((C1*R3)) | (3)
| f_(c2) =1/((2π*R4*C2)) | (4)
| G_1 =R1/R3 | (5)

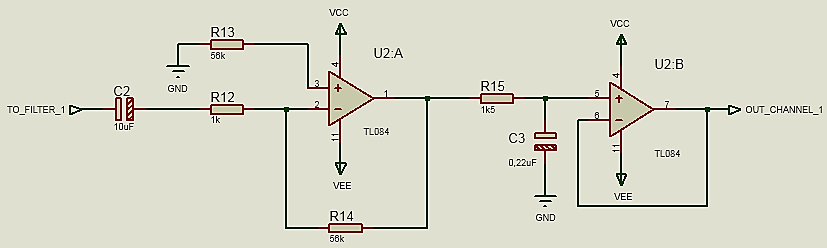
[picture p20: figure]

Figura 8. Circuito de condicionamento do sinal mioelétrico composto por filtros ativos passa-altas (amp-op U1) e passa-baixa (amp-op U2).

A partir dos valores apresentados na figura 8, as frequências das equações 3 e 4 são aproximadamente iguais a 0,4Hz e 500Hz e o ganho G2 da equação 5 é igual a 56. Com isso o ganho final do circuito de aquisição e condicionamento é dado por

| G=G_1 *G_2 =408,8

3.2 TESTES COM PLACA DE CIRCUITO IMPRESSO

A partir do projeto apresentado nas figuras 7 e 8 foi construída uma placa de circuito impresso para captura de sinais mioelétricos, como mostra a figura 9. Para isso foram utilizados os amp-ops do circuito integrado (CI) TL084, da Texas Instruments, representados por U1 e U2. A disposição desses amplificadores nos CIs pode ser observada na figura 10.

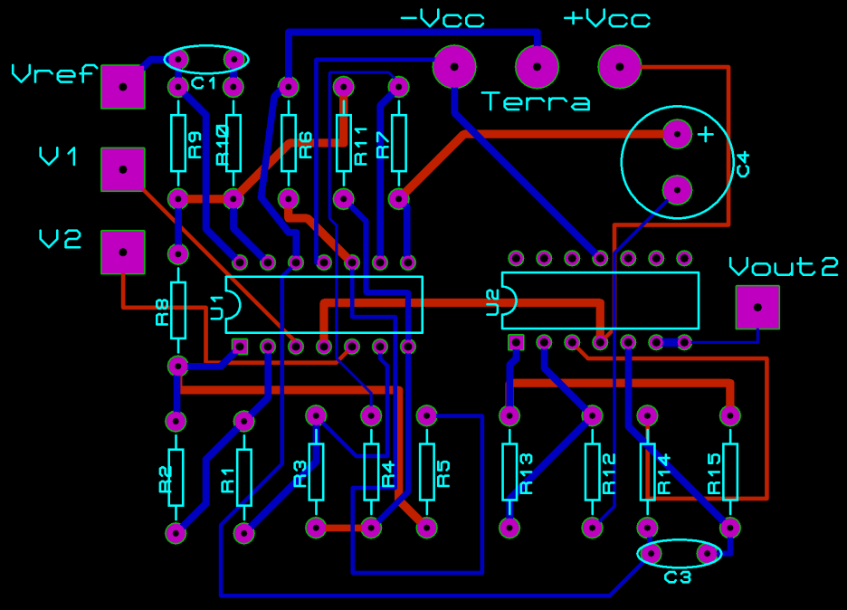
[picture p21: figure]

Figura 9. Desenho do circuito para captura do sinal mioelétrico. As linhas vermelhas encontram-se na face superior da placa enquanto as azuis na parte inferior.

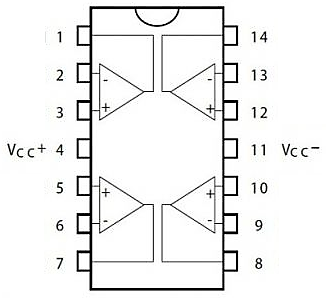
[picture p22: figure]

Figura 10. Disposição dos amplificadores operacionais em um CI TL084, com pinagem enumerada.

Os sinais de teste foram obtidos ao se posicionar os eletrodos de captura no antebraço e o eletrodo de referência nas costas, próximo ao ombro, como mostra a figura 11. Além disso, os CIs foram alimentados com uma fonte simétrica de ±9V.

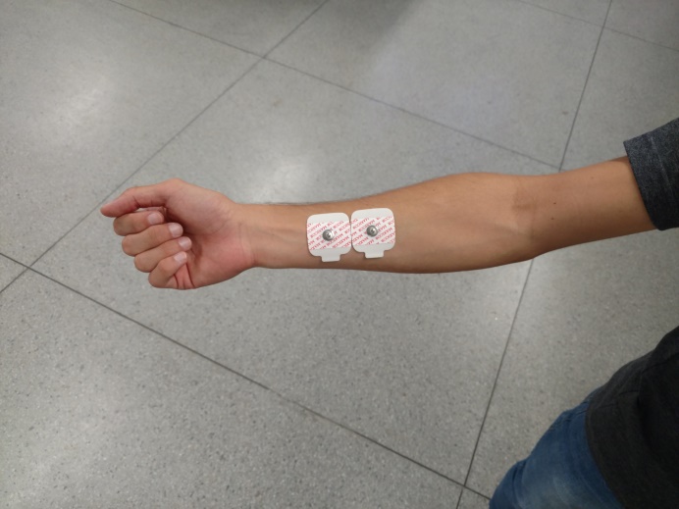
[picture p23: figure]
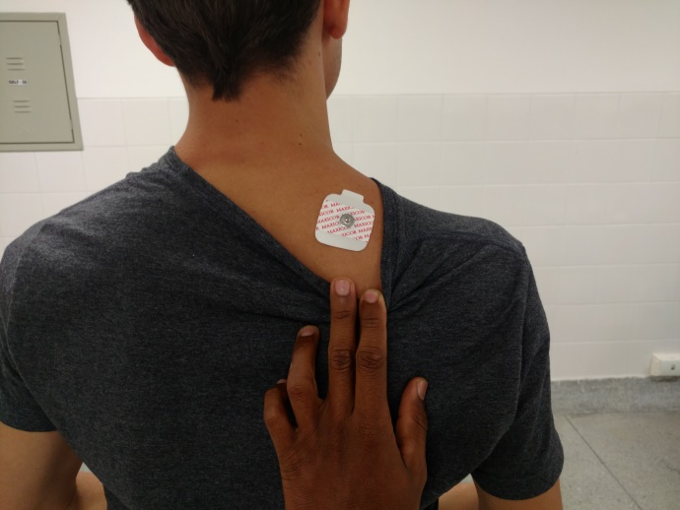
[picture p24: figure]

Figura 11. Posicionamento dos eletrodos de superfície, segundo a configuração bipolar, para captura de um sinal mioelétrico gerado pela atividade muscular no antebraço.

Executando-se movimentos de abertura e fechamento do punho ou de um conjunto de dedos foram capturados, através de um osciloscópio, os sinais mioelétricos apresentados nas figuras 12, 13 e 14. Observa-se que esses atendem as características citadas na seção 2.1 do capítulo 2 deste relatório e também são semelhantes às formas de sinal encontradas em outros trabalhos da literatura [1] [3] [5] [6] [7].

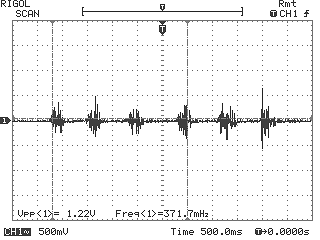
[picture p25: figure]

Figura 12. Captura de sinal mioelétrico no antebraço direito ao se abrir e fechar a mão.

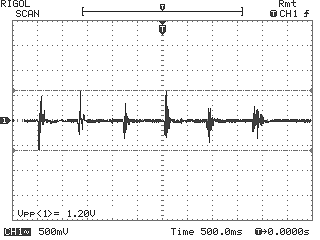
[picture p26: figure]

Figura 13. Captura de sinal mioelétrico no antebraço direito ao se abrir e fechar os dedos anular e mínimo.


Figura 14. Captura de sinal mioelétrico no antebraço direito ao se abrir e fechar os dedos indicador e médio.

3.3 CIRCUITO DE AQUISIÇÃO E CONDICIONAMENTO PARA 4 CANAIS

O projeto do circuito de aquisição e condicionamento simultâneo para 4 sinais mioelétricos foi realizado utilizando-se em cada canal o mesmo projeto apresentado na seção 3.3. Portanto, os valores dos componentes são idênticos, assim como os ganhos dos circuitos de aquisição e condicionamento. Além disso, o circuito de referência foi compartilhado entre os 4 canais. A figura 15 apresenta o modelo 3D do circuito.


Figura 15. Modelo 3D do circuito de aquisição e captura simultânea de 4 sinais mioelétricos.

Os eletrodos de entrada também foram compartilhados entre os canais, visando diminuir o número final de eletrodos a ser utilizado sobre a pele. A figura 16 ilustra essa configuração.


Figura 16. Cada sinal mioelétrico é adquirido através de um canal (C1, C2, C3 e C4), que possui na sua entrada um amplificador de instrumentação, com duas entradas. Ao menos uma entrada de cada canal é compartilhada com um canal vizinho.

3.4 TESTES COM PLACA DE CIRCUITO IMPRESSO PARA 4 CANAIS

Para verificar o funcionamento da placa de circuito impresso para 4 canais, foi preciso converter os dados analógicos para forma digital, enviá-los para um computador e gerar gráficos através de uma interface.

A conversão analógico-digital e o envio dos dados para o computador foi realizado com o auxílio da plataforma programável Tiva TM4C123GLX, apresentado na figura 17. Esse kit possui dois ADCs de resolução e taxa de amostragem máximas de 12 bits e 1GHz, respectivamente. Além disso, provê comunicação serial através de porta USB.


Figura 17. Plataforma programável Tiva TM4C123GLX.

Os sinais mioelétricos dos 4 canais foram quantizados em uma escala de 12 bits e amostrados a uma taxa de 2KHz. Esta taxa foi escolhida baseada no Teorema da Amostragem de Nyquist-Shanon, pois a maior frequência passante do circuito de condicionamento é de 500Hz e o seu dobro (1kHz) é menor do que a taxa de amostragem de 2kHz utilizada. Em seguida, o envio dos dados digitalizados para o computador foi feito através da comunicação serial.

Para exibir as formas de onda em tempo real, desenvolveu-se uma interface em Python, capaz de plotar 4 gráficos simultaneamente. As figuras 18, 19, 20, 21 e 22 mostram exemplos dos gráficos plotados pela interface quando o circuito de aquisição e condicionamento capturou movimentos específicos de uma mão.

Como é possível observar através dos gráficos, cada canal reage de maneira distinta aos movimentos executados e a composição de todas as respostas caracteriza melhor um movimento. Por exemplo, na figura 18, os canais 1 e 2 são os que apresentam maior resposta ao movimento de fechamento do punho, enquanto o canal 3 praticamente não apresenta resposta. Por outro lado, na figura 19, o canal 3 apresenta variações de amplitude mais próximas das observadas nos canais 1 e 2.


Figura 18. Gráficos plotados na interface durante o movimento de fechamento do punho.


Figura 19. Gráficos plotados na interface durante o movimento de contração do pulso.


Figura 20. Gráficos plotados na interface durante o movimento de contração do dedo médio.


Figura 21. Gráficos plotados na interface durante o movimento de contração do dedo indicador.


Figura 22. Gráficos plotados na interface durante o movimento de contração dos dedos anular e mínimo.

4 CONCLUSÃO

A Eletromiografia de Superfície tem uma grande importância em aplicações práticas, como no controle de próteses artificiais. Além disso, continua sendo alvo de pesquisas, pela sua facilidade de utilização. No entanto, necessita de circuitos capazes de lidar com a grande quantidade de ruído que distorce o sinal mioelétrico durante a sua captura.

Este trabalho busca desenvolver um conjunto de hardware e software, de baixo custo, capaz de efetuar a aquisição e o condicionamento de sinais mioelétricos de forma satisfatória. Até o presente momento, foram estudados os fundamentos teóricos necessários para a concepção desse sistema. A partir disso, desenvolveu-se uma placa de captura de um sinal mioelétrico que utiliza a configuração bipolar de eletrodos.

Os resultados obtidos para o circuito de captura de um canal mostraram-se dentro do esperado, pois se assemelham as características do sinal estudado e aos resultados de outros trabalhos da literatura. Além disso, ao se multiplicar o circuito para captura de 4 sinais simultaneamente, compartilhando-se eletrodos e circuito de referência, os sinais obtidos mantiveram suas características e o tempo de resposta do sistema não apresentou atrasos que prejudicassem a visualização dos resultados. As análises preliminares também mostraram que o uso de múltiplos canais favorece a caracterização de movimentos, pois cada canal responde de forma distinta aos diferentes movimentos realizados por uma mão, gerando mais informações sobre eles.

Portanto, os próximos passos consistirão na busca do aprimoramento do circuito de captura de múltiplos sinais mioelétricos, com o intuito de reduzir suas dimensões e adicionar proteções a possíveis falhas. Em paralelo a isto, pretende-se utilizar os dados da captura para um estudo de caracterização e classificação dos movimentos de uma mão, a fim de se controlar uma mão robótica.

REFERÊNCIAS BIBLIOGRÁFICAS

[1] DE LUCA, C.J. Electromyography. Encyclopedia of Medical Devices and Instrumentation, 2 ed., 98-109, 2006.

[2] DE LUCA, C.J. The Use of Surface Electromyghraphy in Biomechanics. Journal of Applied Biomechanics, 13, 135-163, 1997.

[3] BALBINOT, A., JUNIOR, A. S., FAVIEIRO, G. W. Decoding Arm Movements by Myoelectrics Signal and Artificial Neural Networks. Intelligent Control and Automation, 4, 87-93, 2013.

[4] LI, G., SCHULTZ, A.E., KUIKEN, T.A. Quantifying Pattern Recognition – Based Myoeletric Control of Multifunctional Transradial Prosthesis. IEEE Trans. Neural Syst. Rehab. Eng., vol. 18, nº 2, pp. 185–192, 2010.

[5] BASMAJIAN, J.V., DE LUCA, C.J. Muscle Alive: Their Function Revealed by Electromyography. 5 ed., Williams & Wilkins, 1985.

[6] FORTI, F. Análise do Sinal Eletromiográfico em Diferentes Posicionamentos, Tipos de Eletrodos, Ângulos Articulares e Intensidade de Contração. Universidade Metodista de Piracicaba, 2005.

[7] DE LUCA, C.J. Surface Electromyography: Detection and Recording. DelSys Incorporated, 2002.

[8] JUNG, W.G. Op Amp Applications Handbook. 1 ed., Elsevier, 2004.

[9] JUNIOR, A.P. Amplificadores Operacionais e Filtros Ativos. 6 ed., Bookman, 2007.

[10] LOPEZ. S. A. Design and Construction of an EMG Multichannel Acquisition System Prototype. Politecnico Di Torino, 2012.

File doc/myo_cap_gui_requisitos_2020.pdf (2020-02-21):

myo_cap_gui – interface gráfica para digitalização de sinal miográfico

Palavras-chave

miografia, conversão A/D, neurociência

Área de conhecimento

Ciências exatas e da terra - Ciência da Computação - Sistemas de Computação – Processamento Gráfico (Grraphics)

Link do grupo de pesquisa no CNPq

http://dgp.cnpq.br/dgp/espelhogrupo/8003760460683702

Linha de Pesquisa

Visão computacional

### 1. Introdução/Justificativa

Inclua na justificativa os benefícios esperados no processo ensino-aprendizagem dos alunos de graduação e/ou pós-graduação vinculados ao projeto. Explicite também o retorno para os cursos de graduação e/ou pós-graduação e para os professores da UFS em geral.

Através de dispositivos eletrônicos e eletrodos, é possível captar sinais provenientes de nervos motores. Essa técnica é conhecida como miografia. Quando são usados eletrodos sobre a pele, é conhecida como miografia de superfície.

Pelo fato de haver músculo e pele entre o eletrodo e os neurônios de interesse, os sinais obtidos através da miografia de superfície contêm uma grande quantidade de ruído. Através de filtros, é possível eliminar parte do ruído. Técnicas de aprendizado computacional podem ser usadas para classificar os sinais obtidos, vinculando-os a movimentos pré-estabelecidos. Uma vez treinado o classificador, o sinal poderá ser usado para controlar próteses mecânicas.

### 2. Interface myo_cap

### 2.1 Objetivos

O projeto tem como objetivo criar um sistema de software, mais especificamente uma interface gráfica, e firmware que permita que um computador se comunique com a placa TIVA, exiba na tela e salve em arquivo os sinais capturados pela placa. A Figura 1 mostra como deve ser a tela principal da interface gráfica. O sistema deve ser escrito em inglês, já que o trabalho deve ser publicado em veículo internacional no futuro.

A placa TIVA possui 12 conversores A/D, portanto, pode capturar 12 sinais a cada leitura. Será conectada a placas feitas sob medida para capturar sinais miográficos. Cada placa poderá possuir até 12 canais e os sinais podem ser multiplexados caso haja necessidade.

A interface gráfica permitirá a escolha de parâmetros de captura e de exibição. Os parâmetros de captura devem ser transmitidos à placa TIVA por meio de protocolo a ser defnido. Os parâmetros de exibição afetam apenas a visualização do sinal na tela do computador.

O programa salva a série temporal em um vetor na memória. O mesmo vetor é usado quando a série é lida de um arquivo. Ao selecionar Show capture, o programa deve exibir os dados capturados independente se foram lidos do arquivo ou direto da placa.

Para acelerar a alocação e a execução, o vetor deve crescer em blocos ao invés de uma posição por vez. O programa deve ter controle do número de posições usadas do vetor.

A interface gráfica não conhece a configuração do hardware. Deve ser genérica de modo que funcione com qualquer configuração. O usuário, por sua vez, deve ser capaz de indicar a configuração correta do hardware, por exemplo, número de canais a serem lidos e número de placas a serem multiplexadas. A placa TIVA recebe a solicitação e retorna erro ou ok conforme sua capacidade.

Futuramente pode-se definir um conjunto de funções para consultar a placa quanto a suas capacidades e configuração, por exemplo, um cojunto de funções tiva.getMaxY e tiva.getMinY onde Y é um certo parâmetro de captura.

### 2.2. Arquitetura

O programa será escrito em python 2.7 para que seja compatível com as bibliotecas de captura de movimento do LeapMotion. Deve haver ao menos 3 arquivos python:

tiva.py: contém as funções de comunicação com a placa tiva.

win_main.py: contém a implementação da janela principal.

win_settings.py: implementa a caixa de diálogo onde o usário define os parâmetros de captura.

### 2.3. Parâmetros de captura

Os parâmetros de captura são enviados à placa TIVA e são salvos no arquivo CSV. São definidos no início da captura e, para serem modificados, a captura deve ser interrompida.

As funções definidas abaixo retornam um par (0, “”) em caso de sucesso. Retornam um inteiro diferente de zero e uma mensagem em caso de erro. A mensagem é enviada pelo firmware da placa TIVA, permitindo ao usuário saber o que a placa suporta, e corrigindo os

parâmetros de acordo.

Os inteiros representam códigos de erro previamente estabelecidos. A mensagem deve ser informativa, explicitando o que saiu errado. Por exemplo: caso um parâmetro esteja fora dos valores suportados, indicar na mensagem qual é o intervalo como em:

tiva.setBps: Error: BPS value = 16 outside supported interval [8..12].

Bits per sample (k in bps, integer): indica o número de bits por amostra. O intervalo dinâmico L é função de k, dado por 2^k. Por exemplo, 8 bps correspondem a um intervalo dinâmico de 256 valores. Deve haver uma função tiva.setBps(k) que envia o valor de bps desejado. Note que mesmo capturando em 12 bits, mandará apenas os 8 mais significativos se esse for o falor de k. O firmware retornará erro caso k seja menor que 8 ou maior que 12.

Sample rate (r in Hz): indica a taxa de amostragem em amostras por segundo. Deve haver uma função tiva.setSampleRate(rate) que envia o valor de bps desejado. O firmware retornará erro caso r esteja fora do intervalo permitido.

Channels per board (c, integer): indica o número de canais a serem lidos por placa. A placa não é capaz de detectar quantos canais estão disponíveis, portanto, serão lidos os sinais dos c primeiros conversores A/D da TIVA. Deve haver uma função tiva.setNChannels(c) que define quantos canais devem ser lidos. O firmware retornará erro caso c seja menor que 1 ou maior que 12.

Number of boards (n, integer): indica o número de placas a TIVA deve multiplexar. O valor padrão é 1. Deve haver uma função tiva.setNBoards(n) que define quantos canais devem ser lidos. O firmware retornará erro caso n seja menor que 1 ou maior que 8, já que usaremos 3 vias de seleção. Não precisa necessariamente ser potência de 2. Podemos multiplexar 3 placas, por exemplo.

Note que, caso o hardware mude no futuro, ou caso usemos mais de um hardware alternativo, o firmware deve ser adaptado e não a interface gráfica. A interface deve ser o mais genérica possível.

### 2.4. Parâmetros de exibição

Os parâmetros de exibição não são enviados à placa TIVA. Podem ser modificados a qualquer momento e não interferem na captura dos sinais.

Swipe (t in seconds, float. w in samples, integer): indica o tempo/número de amostras em uma varredura horizontal da tela. O valor padrão é 1s. É dado por duas caixas de texto na tela: uma com o tempo em segundos (t) e outra com o número de amostras (w). Obviamente, w = t*r. O valor de um muda automaticamente com a mudança do outro.

Minimum Voltage (voltMin, float): indica a voltagem correspondente à intensidade 0.

Maximum Voltage (voltMax, float): indica a voltagem correspondente à intensidade L, onde

L é o tamanho do intervalo dinâmico, dado por 2^k, e k é o número de bits por amostra.

Vertical Tick (vertTick in Volts, float): intervalo entre as linhas horizontais pontilhadas do grid. O valor padrão é 1.0V

Horizontal Tick (horizTick in seconds, float): intervalo entre as linhas verticais pontilhadas do grid.

Channels (z, integer): permite a exibição de mais canais na tela. O número padrão é 4. Caso não caibam todos os canais sendo capturados, deve haver um scroll bar.

### 2.5. Menus

Menu File

Load capture: carrega arquivo de captura CSV previamente salvo. Save capture: salva dados capturados em arquivo CSV.

Menu capture

Start capture: inicia a captura. Desabilita a alteração dos parâmetros de captura. Stop capture: para a captura. Habilita a alteração dos parâmetros de captura. Show capture: exibe os dados previamente capturados.

Menu settings

Load settings: carrega arquivo com os parâmetros de captura e exibição.
Save settings: salva arquivo com os parâmetros de captura e exibição.
Capture settings: abre diálogo para edição dos parâmetros de captura: Bits per sample, Sample rate, Channels per board, Number of boards.
Display settings: abre diálogo para edição dos parâmetros de exibição: Swipe, Zero, Amplitude, Vertical tick, Horizontal tick e Channels.
Communication settings: abre diálogo para edição dos parâmetros de comunicação com a placa, ou seja, número da porta serial, tamanho do pacote de dados e modo packed/unpacked.

### 2.6. Parâmetros de comunicação

Os parâmetros de comunicação estabelecem como será a comunicação com a porta serial.

Número da porta serial

Baud rate: o baud rate padrão é característica específica da placa. A classe que implementa os parâmetros específicos da placa deve conter um baud rate funcional para a comunicação inicial e possível seleção de novo baud rate.

Tamanho do pacote de dados: estabelece o tamanho do pacote que transporta os dados de captura da placa para a porta serial.

Modo packed/unpacked: seleciona o modo de comunicação dos dados. Deve haver flags constantes na classe dos parâmetros especificos da placa, MODE_PACKED_AVAILABLE e MODE_UNPACKED_AVAILABLE com valores diferentes de zero caso os modos respectivos estejam disponíveis. O modo packed é selecionável caso MODE_PACKED_AVAILABLE seja diferente de zero.

### 2.7. Arquivo de saída CSV

Armazena os dados da captura, uma amostra por linha e colunas separadas por ponto e vírgula. Nas primeiras linhas armazena metadados com as configurações da captura, tanto de EMG quanto dos gestos. As linhas com metadados começam com um único sinal de #.

Linhas com comentários começam com dois sinais de # e são ignoradas.

Abaixo está um exemplo de arquivo de saída.

## File generated by myo_cap software

## Available from github.com/ddantas/myo_cap ## Timestamp: 2018-05-23_20-57-32

## EMG capture settings

# sampleRate: 2000

# channelsPerBoard: 4

# nBoards: 1

# bitsPerSample: 12

## Data

t; ch0; ch1; ch2; ch3
0.0000; 2048; 2048; 2048; 2048 0.0005; 2047; 2048; 2049; 2048 0.0010; 2047; 2048; 2049; 2048 0.0015; 2048; 2047; 2048; 2049

### 2.8. Arquivo de configurações

Usa o mesmo formato dos metadados do arquivo de saída. Armazena as configurações de exibição e emulação de EMG.

## File generated by leap_cap software

## Available from github.com/ddantas/leap_cap

## Timestamp: 2018-05-23_20-57-32

## EMG capture settings

# sampleRate: 2000

# channelsPerBoard: 4

# nBoards: 1

# bitsPerSample: 12

## EMG display settings

# swipeSamples: 2000

# vMin: -3.3

# vMax: 3.3

# vertTick: 1.0

# horizTick: 200

# showChannels: 4


Figura 1: aspecto da interface gráfica.

### 3. Interface leap_cap

### 3.1. Objetivos

Este projeto tem como objetivo criar um sistema de software, mais especificamente uma interface gráfica, que permita a captura simultânea de sinais de eletromiografia (EMG) e gestos feitos pela mão de um usuário do sistema.

A captura de sinais de EMG será feita através de um dispositivo de captura especializado. O dispositivo é composto por uma TivaWare, responsável pela conversão A/D, placas de captura, multiplexação, cabos e eletrodos, dispostos sobre a superfície do braço do usuário. Alternativamente, o sistema pode usar como entrada um arquivo CSV com os sinais de EMG, permitindo o teste do sistema sem a presença do dispositivo.

A captura de gestos poderá ser feita de duas maneiras diferentes. A mais simples será através de um teclado, capaz de indicar quais dedos estão pressionando uma tecla. Outra maneira mais sofisticada será através do LeapMotion, um dispositivo capaz de capturar com boa precisão o quanto está flexionado cada um dos dedos da mão do usuário.

O dispositivo e respectivo software de captura estão em desenvolvimento e disponíveis no github. Já existem protótipos com um e quatro canais funcionais. Existem também um protótipo do software capaz de capturar e salvar em arquivo os sinais de EMG. As especificações do hardware e código fonte do software estão no link abaixo:

https://github.com/ddantas/myo_cap

O aluno responsável por esse projeto deve, na medida do possível, aproveitar o código fonte já disponível, evitando refazer o que é responsabilidade de outros alunos, mais especificamente, código relacionado à captura e exibição de sinais de EMG: escolha de parâmetros de captura de sinais de EMG, comunicação com o dispositivo de EMG, escolha de parâmetros de exibição de sinais de EMG.

Deve portanto focar em criar as funções de captura de gestos pelo teclado e LeapMotion, e na implementação da interface gráfica que exibirá os gestos a serem realizados pelo usuário.

### 3.2. Arquitetura

O programa será escrito em python 2.7 para que seja compatível com as bibliotecas de captura de movimento do LeapMotion. Deve haver ao menos 3 arquivos python:

leap.py: contém as funções de comunicação com o LeapMotion.

win_main.py: contém a implementação da janela principal.

win_gesture_settings.py: implementa a caixa de diálogo onde o usário define os parâmetros de captura.

### 3.3. Parâmetros de captura de sinais de EMG

Tanto a interface gráfica para definir os parâmetros de captura quanto as funções que enviam os parâmetros para a placa devem ser aproveitadas do sistema de captura de EMG.

Os parâmetros de captura são enviados à placa TIVA e são salvos no arquivo CSV. São definidos no início da captura e, para serem modificados, a captura deve ser interrompida.

Para mais detalhes, ver Seção 2.3.

### 3.4. Parâmetros de exibição de sinais de EMG

A interface gráfica para exibir e definir os parâmetros de exibição de sinais de EMG devem ser aproveitadas do sistema de captura de EMG.

Para mais detalhes, ver Seção 2.4.

### 3.5. Parâmetros de captura de gestos

Os parâmetros de captura de gestos são salvos, juntamente com os parâmetros de captura de sinal de EMG, no arquivo CSV.

Device: LeapMotion ou Keyboard.

Routine: nome de arquivo contendo a rotina de captura, ou seja, a sequência de gestos. O formato é definido na Seção 3.7. Rotina de captura.

Hand: especificação da mão a ser capturada. Valores possíveis: {L, R} para esquerda ou direita.

### 3.6. Menus

Menu File

Load capture: carrega arquivo de captura CSV previamente salvo.
Save capture: salva dados capturados em arquivo CSV.
Load EMG signal: carrega dados de EMG para emular o uso do dispositivo de captura de sinais de EMG, permitindo testar o sistema mesmo sem o dispositivo.

Menu Capture

Start capture: inicia a captura. Desabilita a alteração dos parâmetros de captura. Stop capture: interrompe a captura. Habilita a alteração dos parâmetros de captura. Show capture: exibe dados de gestos e EMG previamente capturados.

Menu Settings

Load settings: carrega arquivo com os parâmetros de captura e exibição.
Save settings: salva arquivo com os parâmetros de captura e exibição.
EMG capture settings: abre diálogo para edição dos parâmetros de captura de EMG: Bits per sample, Sample rate, Channels per board, Number of boards.
EMG display settings: abre o diálogo para edição dos parâmetros de exibição do sinal de EMG: Swipe, Zero, Amplitude, Vertical tick, Horizontal tick e Channels.
EMG communication settings: abre diálogo para edição dos parâmetros de comunicação com a placa, ou seja, número da porta serial, tamanho do pacote de dados e modo packed/unpacked.
EMG emulation: Menu com checkbox. Caso habilitado, é necessário carregar um arquivo de sinal de EMG. Exibe diálogo com mensagem: “Please load EMG signal by acessing menu File > Load EMG signal”
Gesture capture settings: abre diálogo para edição dos parâmetros de captura de gestos: Device, Routine, Hand side.

### 3.7. Rotina de captura

A rotina de captura especifica quais gestos serão capturados e por quanto tempo. É um arquivo CSV com duas colunas: a primeira indica o gesto a ser feito e a segunda o tempo em segundos. Linhas em branco ou iniciadas com o caractere # são ignoradas.

Os gestos são compostos por duas palavras unidas por underscore (_). A primeira indica os dedos a serem movimentados e a segunda indica o movimento.

A primeira palavra pode ser uma das seis a seguir: {hand} ou {1th, 2in, 3md, 4an, 5mn}, correspondentes aos cinco dedos, polegar, indicador, médio, anular e mínimo.

A segunda palavra pode ser uma das quatro a seguir: {open, close} ou {flex, curl, flex_curl}, correspondentes a todos os dedos esticados, todos os dedos flexionados, primeira articulação flexionada, segunda e terceira articulações flexionadas e três articulações flexionadas.

Todas as combinações possíveis são dadas pela união dos produtos cartesianos entre os conjuntos {hand} X {open, close} e {1th, 2in, 3md, 4an, 5mn} X {flex, curl, flex_curl}, totalizando 17 gestos.

Abaixo está um exemplo de arquivo de rotina de captura.

hand_open;2
hand_close;2
hand_open;2
hand_close;2

## 1 - thumb

1th_flex;2
hand_open;2
1th_flex;2
hand_open;2
1th_flex_curl;2
hand_open;2
1th_flex_curl;2
hand_open;2

### 3.8. Arquivo de saída CSV

Armazena os dados da captura, uma amostra por linha e colunas separadas por ponto e vírgula. Nas primeiras linhas armazena metadados com as configurações da captura, tanto de EMG quanto dos gestos. As linhas com metadados começam com um único sinal de #.

Linhas com comentários começam com dois sinais de # e são ignoradas.

Abaixo está um exemplo de arquivo de saída.

## File generated by leap_cap software

## Available from github.com/ddantas/leap_cap ## Timestamp: 2018-05-23_20-57-32

## EMG capture settings

# sampleRate: 2000

# channelsPerBoard: 4

# nBoards: 1

# bitsPerSample: 12

## Gesture capture settings ##

# device: keyboard

# routine: default.csv

# hand: right

## Data

th_flex; th_curl; in_flex; in_curl; md_flex, md_curl; an_flex; an_curl; mn_flex; mn_curl; ch0; ch1; ch2; ch3
0; 0; 0; 0; 0; 0; 0; 0; 0; 0; 2048; 2048; 2048; 2048
0; 0; 0; 0; 0; 0; 0; 0; 0; 0; 2048; 2048; 2048; 2048
0; 0; 0; 0; 0; 0; 0; 0; 0; 0; 2048; 2048; 2048; 2048 100; 100; 0; 0; 0; 0; 0; 0; 0; 0; 2048; 2048; 2048; 2048 ...

### 3.9. Arquivo de configurações

Usa o mesmo formato dos metadados do arquivo de saída. Armazena as configurações de exibição e emulação de EMG.

## File generated by leap_cap software

## Available from github.com/ddantas/leap_cap

## Timestamp: 2018-05-23_20-57-32

## EMG capture settings

# sampleRate: 2000

# channelsPerBoard: 4

# nBoards: 1

# bitsPerSample: 12

## EMG display settings

# swipeSamples: 2000

# vMin: -3.3

# vMax: 3.3

# vertTick: 1.0

# horizTick: 200

# showChannels: 4

## EMG emulation settings

# emulationFlag: true

# emulationData: 2018-05-04_14-39-15.csv ##

## EMG communication settings

# comPort: 3

# packetSize: 500

## Gesture capture settings ##

# device: keyboard

# routine: default.csv

# hand: right

### 4. Classe textfile

A classe textfile será usada para salvar e carregar os arquivos de configurações e de captura. Permite que várias threads salvem dados em um único arquivo. Sua interface é dada pelas funções a seguir.

message_save: adiciona mensagem com cada linha precedida de "## " message_save(string msg)

metadata_*_save: adiciona metadado com linha precedida de "# " metadata_text_save(string msg, string value) metadata_number_save(string msg, double value, string format)

metadata_load: lê valor de metadado e retorna em formato de string. metadata_load(string msg, string value)

init: inicializa log, definindo o número de colunas, formato de impressão, e nomes das colunas. Retorna um índice, começando por 1, do grupo de colunas. Pode ser chamando mais de uma vez, caso em que várias threads adicionam colunas diferentes simultaneamente.
format = "%f; %f; %f; %f;"
name_cols = "ch0; ch1; ch2; ch3;"
id = init(int num_cols, string format, string name_cols)

Caso estejamos usando duas placas de 4 canais:

format = "%f;%f;%f;%f;%f;%f;%f;%f"
name_cols = "ch0; ch1; ch2; ch3;ch4; ch5; ch6; ch7"

log: recebe vetor de double e grava na memória na linha correspondente do log. log(int id, double values[])

save: grava log em arquivo.
save(filename)

### 5. Gerador de função

O gerador de função, a ser implementado na TIVA, tem como objetivo testar o sistema sem a necessidade do uso da placa de aquisição e dos eletrodos. A partir do início da captura, um timer é iniciado e o valor da função é calculado em função do timestamp, e não do índice da amostra. Isso permitirá detectar se pacotes de dados estão sendo perdidos.

A amplitude pico a pico deve ser sempre 4096, ou seja 2 elevado ao número de bits do ADC. Clicar em um item do menu adiciona um "check" e envia a função selecionada para a TIVA. Clicar novamente remove o "check" e envia uma mensagem para a Tiva selecionando o ADC.

Na TIVA, uma versão de alto nível do gerador de função deve receber o timestamp, período e forma de onda. A depender da forma de onda, outra função deve ser chamada. Caso o usuário tenha escolhido receber menos bits que os retornados pelo ADC, tanto o valor retornado pelo ADC quanto pelo gerador de função deve sofrer um shift right de tamanho adequado. A operação deve ser implementada de modo que tanto o ADC quanto o gerador de função usem o mesmo código.

### 5.1. Menus

Menu Function Generator

Settings: abre uma caixa de diálogo para definir a frequência da onda e tempo em segundos do stress test.
Square wave (checkable): seleciona modo square wave.
Sine wave (checkable): seleciona modo sine wave.
Sawtooth wave (checkable): seleciona modo sawtooth wave.
Start stress test: inicia stress test. O teste consiste em fazer o streamming de amostras pelo tempo selecionado em settings. Durante o teste, exibir uma progress bar. Ao final, uma caixa de diálogo com uma mensagem como a do exemplo abaixo deve ser exibida:
Test length: | 30s
Capture frequency: | 2000Hz
Expected samples: | 60000
Received samples: | 55320
Dropped samples: | 4680
Drop rate: | 7.80%

### 6. Protocolo de comunicação

O protocolo de comunicação entre a TIVA e a interface Python se divide em dois tipos de mensagens: requisições para a TIVA e mensagens de resultado.

### 6.1. Requisições para a TIVA

As mensagens de requisições possuem seis bytes de comprimento. Os dois primeiros bytes representam uma instrução e os quatro últimos um operando.

Instrução | Operando | Comentário
ai | N/A | Start streamming
as | N/A | Stop streamming
sr | uint32 | Set sample rate in Hz
sc | uint32 | Set number of channels per board
sb | uint32 | Set number of boards
ss | uint32 | Set number of bits per sample
sp | uint32 | Set packet size in bytes
sm | uint32 | Set mode packed or unpacked
sf | float32 | Set function generator wave frequency
gr | N/A | Get sample rate in Hz
gc | N/A | Get number of channels per board
gb | N/A | Get number of boards
gs | N/A | Get number of bits per sample
gp | N/A | Get packet size in bytes
gm | N/A | Get mode packed or unpacked
gf | N/A | Get function generator wave frequency
fa | N/A | Select ADC mode
fq | N/A | Select square wave function mode
fn | N/A | Select sine wave function mode
fw | N/A | Select sawtooth wave function mode

O parâmetro p = packet size define o tamanho em bytes dos pacotes retornados durante uma captura de EMG. O número de instantes capturados I é

I = floor(p /(c*b*s/8))

e o número total de amostras, igual a

I * c * b

onde p = packet size in bytes, c = number of channels, b = number of boards, s = bits per sample.

### 6.2. Mensagens de resultado

As mensagens de resultado devem ser capazes de retornar os resultados das funções de get e mensagens de erro caso o comando não seja reconhecido ou caso algum valor de set esteja fora do intervalo permitido.

Como o tamanho das mensagens agora é variável, é necessário especificar o tamanho da mensagem quando a insttrução for dos tipos me, mw ou ms.

Instrução | Op. 1 | Op. 2 | Comentário
vu | uint32 | N/A | Value of type uint32
vf | float32 | N/A | Value of type float32
me | uint32 | string | Message length; Error message
mw | uint32 | string | Message length; Warning message
ms | uint32 | string | Message length; Streaming packet

Seguem alguns exemplos de mensagens de erro:

tiva.setBps: Error: BPS value = 16 outside supported interval [8..12].

tiva.setSampleRate: Error: sample rate value = -100 outside supported interval [1..4000000].

tiva.setNumBoards: Error: number of boards = 12 outside supported interval [1..6].

tiva.setNumChannels: Error: number of channels = -5 outside supported interval [1..4].

tiva.parseCommand: Warning: instruction = “aa” unknown.

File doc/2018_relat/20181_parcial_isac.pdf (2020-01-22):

## UNIVERSIDADE FEDERAL DE SERGIPE CENTRO DE CIÊNCIAS EXATAS E TECNOLOGIA

## COORDENAÇÃO DE PESQUISA

PROGRAMA INSTITUCIONAL DE BOLSAS DE INICIAÇÃO CIENTÍFICA - PIBIC

## PROCESSAMENTO E CLASSIFICAÇÃO DE SINAL DE MIOGRAFIA

Área do conhecimento: Eletromiografia

Subárea do conhecimento: Eletromiografia de superfície Especialidade do conhecimento: Interatividade e acessibilidade (Graphics)

## Relatório Parcial

### Este projeto é desenvolvido com bolsa de iniciação científica PIBIC/CNPq

São Cristóvão – Sergipe

2018

# Sumário

1

# Atividades Realizadas

Os seis primeiros meses de desenvolvimento deste trabalho foram baseados no cronograma de atividades da Tabela 1. Portanto, nessa primeira fase buscou-se projetar e implementar, em Python, um software de captura de sinais mioelétricos a partir da plataforma de aquisição MyoCap. Essa plataforma foi desenvolvida previamente, como projeto de iniciação científica, para que fosse possível a realização deste plano de trabalho.

Além de um software de captura, também foi necessário implementar um firmware, na linguagem C, para placa Tiva TM4C123G, responsável pela digitalização e envio dos sinais para um computador. Com isso, também foi preciso um estudo sobre como programar microcontroladores.

Atividade | 2017 Ago Set Out Nov Dez | 2018 Jan Fev Mar Abr Mai Jun Jul
Atividade 1 | x x x x x
Atividade 2

Tabela 1 – Cronograma de atividades. Atividade 1: Implementação do software de captura. Atividade 2: Implementação da rede neural.

2

# Justificativas de Alteração no Plano de Tra-

# balho

Não houve alterações de grande relevância neste plano de trabalho. Apenas incluiu-se o desenvolvimento de uma camada de firmware, para que os sinais fossem digitalizados e enviados para um computador. Neste sentido, também foi necessário um estudo sobre microcontroladores, a fim de aprender como programá-los e selecionar qual dispositivo atenderia as necessidades da aplicação. Além disso, foi preciso projetar um circuito capaz de adequar os sinais de saída da MyoCap às entradas da placa Tiva.

3

# Outras Atividades

Durante a primeira etapa de execução deste plano de trabalho foi redigido um artigo para submissão no IEEE Symposium on Computers and Communications (ISCC), que ocorrerá em Junho de 2018, na cidade de Natal. O título do artigo é Low cost hardware and software platform for multichannel surface electromyography (Plataforma de hardware e software de baixo custo para eletromiografia de superfície multicanal), que aborda também em seu conteúdo o firmware e o software de captura desenvolvidos até o momento.

A submissão foi realizada no mês de Janeiro e em Março é esperado o resultado de aceitação.

4

# Revisão da Literatura

O corpo humano pode ser considerado uma “máquina” perfeita, no sentido de que todas as suas partes trabalham em harmonia umas com as outras. A maioria das pessoas controla essa máquina naturalmente no seu dia a dia, exceto quando um distúrbio é provocado, devido a doenças ou lesões que resultem na perda de funcionalidades do corpo.
A ausência de membros é um exemplo de distúrbio que modifica profundamente a vida de uma pessoa, pois tarefas simples como caminhar e segurar objetos com as mãos podem tornar-se extremamente difíceis ou impossíveis de serem executadas. Por isso, uma das soluções adotadas para restabelecer parte desse tipo funcionalidade perdida é o uso de membros artificiais.

Desde a criação dos primeiros membros artificiais, um dos grandes desafios dos pesquisadores tem sido o aperfeiçoamento destas ferramentas, a fim de que possam ser controladas da maneira mais natural possível pelos pacientes (De Luca, 1997; BALBINOT; JÚNIOR; FA-

VIEIRO, 2013; LI; SCHULTZ; KUIKEN, 2010). O controle atual dessas próteses baseia-se principalmente na análise de duas classes de fontes de sinais: biomecânica e bioelétrica. Na biomecânica são considerados estudos sobre o movimento de partes do corpo, as alterações nas propriedades de um componente do corpo como resultado de uma atividade mecânica e o controle do fluxo de ar. Já na bioelétrica são analisados sinais elétricos resultantes de atividades cerebrais, neurais, oculares e musculares – que são os sinais de interesse para este trabalho.

O estudo da dinâmica muscular baseia-se num princípio estabelecido há mais de 200 anos por Galvani (GALVANI, 1791), segundo o qual um músculo esquelético estimulado eletricamente se contrai e, por outro lado, produz corrente elétrica quando se contrai voluntariamente. Essa ideia também é o principal fundamento da Eletromiografia, disciplina que lida com a detecção, a análise e o uso do sinal elétrico que emana da contração muscular, também chamado de sinal miolelétrico.

A Eletromiografia de Superfície possibilita a aquisição desse sinal sem procedimentos invasivos, utilizando eletrodos sobre a pele – conhecidos como eletrodos de superfície (De Luca,

Capítulo 4. Revisão da Literatura | 6

2006) – na região de interesse. Porém, uma das desvantagens desse método é a presença de uma quantidade maior de ruído do que nos métodos invasivos, distorcendo o sinal mioelétrico, já que ele não é adquirido diretamente do músculo.
Para lidar com esse tipo de problema é necessário utilizar amplificadores diferenciais e filtros que atenuem artefatos fora da faixa de frequência do sinal mioelétrico. Produtos comerciais, como o MyoWare (SparkFun Electronics, 2018) são capazes de adquirir sinais mioelétricos dessa maneira. Essa plataforma disponibiliza na sua saída o sinal amplificado, sem uma etapa de conversão Analógico-Digital (A/D). Além disso, possui apenas um canal de aquisição, o que não é almejado por projetos que busquem informações suficientes para o controle de próteses robóticas.

Uma opção mais versátil é proposta por Supuk (SUPUK; SKELIN; CIC, 2014). Sua plataforma possui 8 canais de captura simultânea de sinais mioelétricos. A conversão A/D é feita pela placa PCI-6034E, da Texas Instrumentes, que possui um alto custo e requer um computador desktop para sua utilização.

Em busca de uma maior versatilidade para aplicações que exijam múltiplos canais, foi desenvolvida a plataforma MyoCap (SILVA, 2017), como projeto de iniciação científica do Programa Institucional de Bolsas de Iniciação Científica (PIBIC) entre os anos de 2016 e 2017. Essa plataforma é capaz de realizar a aquisição de 4 sinais mioelétricos simultaneamente.

Neste plano de trabalho, busca-se utilizar a plataforma MyoCap para captura de sinais mioelétricos e, em seguida, digitalizar esses sinais para que sejam visualizados em uma interface gráfica e analisados futuramente para o controle de próteses robóticas.

5

# Metodologia

Esta seção apresentará os detalhes da arquitetura e da implementação do sistema para aquisição de sinais mioelétricos. A Figura 1 mostra a arquitetura do sistema proposto.

Observa-se que os eletrodos devem ser aderidos sobre a pele humana e conectados a entrada da MyoCap, que apresentará em sua saída os sinais mioelétricos na sua forma analógica. Em seguida, esses sinais serão adequados através de um somador inversor para que possam ser recebidos pela placa Tiva. Nessa placa, há um firmware responsável pela conversão A/D dos sinais e envio dos dados para um computador, via comunicação USB. No computador, os dados serão recebidos pelo software de aquisição e exibidos em uma interface gráfica.


Figura 1 – Diagrama de blocos do sistema proposto.

## 5.1 MyoCap

A MyoCap é uma placa para aquisição múltipla de sinais mioelétricos. Ela é capaz de oferecer até 4 sinais, amplificados e com banda passante de frequência de 20Hz a 500Hz, que é a faixa de frequência indicada para aquisição desse tipo de sinal (De Luca, 2006). Os sinais

Capítulo 5. Metodologia | 8

mioelétricos disponibilizados por essa plataforma possuem amplitude entre -1.0V e 1.0V. A Figura 2 apresenta a placa de circuito impresso com seus respectivos componentes soldados.


Figura 2 – Placa de aquisição MyoCap.

## 5.2 Somador inversor

Como os sinais oferecidos pela MyoCap possuem níveis de tensão negativos e a placa Tiva suporta em seus pinos de entrada analógica tensões na faixa de 0V a 3.3V, foi necessário utilizar um somador inversor que adequasse as saídas da MyoCap às entrada da Tiva. A Figura 3 mostra o circuito do somador inversor utilizado para o canal 1 da MyoCap e esse mesmo circuito foi replicado para os demais canais. A Equação 5.1 descreve a relação entre as tensões Vo de saída e Vi de entrada do somador.

A entrada Vi do somador foi conectada ao terminal de saída OUT_CHANNEL_1 do primeiro canal da MyoCap. A saída Vo do somador foi conectada ao pino analógico TO_TIVA da placa Tiva. Como a alimentação do sistema foi feita através de baterias de 9V, os valores de VCC e VEE são, respectivamente, 9V e -9V. Assim, utilizando-se os valores de resistência informados na Figura 3, foram adicionados 1.6V ao canal 1 da MyoCap, resultando em um sinal mioelétrico de 0.6V a 2.6V de amplitude sendo aplicado no pino analógico da Tiva.

Vo = −(

R16

R17

Vi +

R16

R18

VEE) | (5.1)

## 5.3 Placa Tiva

A placa de desenvolvimento Tiva EK-TM4C123GLX é responsável pela conversão A/D do sinal mioelétrico e comunicação USB com um PC. Essa plataforma possui um baixo custo ($15) e algumas das suas características são: processador ARM Cortex M4 de 32 bits e 80MHz,

dois conversores A/D com resolução máxima de 12 bits e taxa de amostragem máxima de 1GHz, 12 pinos analógicos de entrada e interface USB para comunicação (Texas Instruments Incorporated, 2014). A Figura 4 apresenta essa plataforma.

Capítulo 5. Metodologia | 9


Figura 3 – Circuito somador inversor de tensão.

O firmware desenvolvido nessa placa leva em consideração o Teorema da Amostragem de Nyquist-Shannon que diz que a taxa de amostragem de um sinal precisa ser, no mínimo, duas vezes maior que a frequência mais alta do sinal. No entanto, na prática recomenda-se uma taxa de amostragem de quatro a cinco vezes maior. Como a frequência mais alta do sinal mioelétrico é de 500Hz, a taxa de amostragem ideal a ser utilizada encontra-se na faixa de 2kHz a 2.5kHz (Motion Lab Systems Inc., 2009). Para este trabalho utilizou-se a taxa de 2kHz e uma resolução de 12 bits para o conversor A/D. Em seguida, os dados digitalizados foram transferidos para um computador através da interface USB da placa.


Figura 4 – Placa de desenvolimento Tiva EK-TM3C123GLX.

## 5.4 Software de captura

O software de captura de sinais mioelétricos foi desenvolvido em Python e possibilitou na primeira etapa deste plano de trabalho: a visualização de todos os sinais simultaneamente em uma interface gráfica, a modificação de parâmetros de exibição para que os gráficos atendessem as necessidades de um usuário e o armazenamento dos dados - pois futuramente serão utilizados para classificação de gestos de uma mão robótica.

Os parâmetros de exibição utilizados foram:

- Swipe: indica o número de amostras em uma varredura horizontal da tela;

Capítulo 5. Metodologia | 10
- Position: indica a posição, em Volts, do eixo horizontal dos canais;
- Horizontal Tick (HTick): intervalo horizontal entre as marcações pontilhadas da grade;
- Vertical Tick (VTick): intervalo ertical entre as marcações pontilhadas da grade;
- Channels: número de canais a serem exibidos.

Na próxima etapa deste trabalho, espera-se incluir no software um protocolo que possibilite o envio de comandos para Tiva, a fim de modificar também parâmetros de captura, como a taxa de amostragem. Além disso, também pretende-se adicionar a opção de aplicação de filtros digitais aos sinais, com a finalidade de atenuar interferências que não foram completamente eliminadas pela MyoCap.

6

# Resultados preliminares

Utilizando-se eletrodos de superfície e a MyoCap, como mostra a Figura 5, foram adquiridos 4 sinais mioelétricos de um antebraço esquerdo. A relação entre cada canal de saída e os eletrodos de entrada é dada pelas Equações 6.1, 6.2, 6.3, 6.4. Um sexto eletrodo foi aderido à região da vértebra C7, para servir como referência para as capturas (HERMENS et al., 2000).

Ch1 = IN1−IN2 | (6.1)
Ch2 = IN2−IN3 | (6.2)
Ch3 = IN3−IN4 | (6.3)
Ch1 = IN4−IN5 | (6.4)


Figura 5 – Disposição dos eletrodos no antebraço esquerdo para aquisição com a MyoCap.

Capítulo 6. Resultados preliminares | 12

As saídas dos canais da MyoCap foram conectadas a somadores inversores, implementados em uma protoboard a partir do circuito integrado TL084, da Texas Instruments. Em seguida, as saídas dos somadores foram conectados aos pinos analógicos da placa Tiva, para que os sinais fossem digitalizados e enviados, através da porta USB, para um computador.

O software de captura foi capaz de exibir, em tempo real, os sinais mioelétricos dos 4 canais da MyoCap durante movimentos repetidos de fechamento e abertura do punho esquerdo. A Figura 6 apresenta a janela de aquisição durante os testes e a Figura 7 apresenta a janela de edição dos parâmetros de exibição com os valores setados para gerar esse resultado.


Figura 6 – Software de captura plotando os gráficos das saídas dos 4 canais da MyoCap, durante o movimento de fechamento e abertura do punho esquerdo.


Figura 7 – Janela de edição dos parâmetros de exibição do software de captura, com os valores setados para aquisição dos resultados da Figura 6.

# Referências

BALBINOT, A.; JÚNIOR, A. S.; FAVIEIRO, G. W. Decoding Arm Movements by Myoelectric Signal and Artificial Neural Networks. Intelligent Control and Automation, v. 4, n. 1, p. 87–93, 2013. ISSN 2153-0653. Citado na página 5.

De Luca, C. J. The use of surface electromyography in biomechanics. Journal of applied biomechanics, v. 13, p. 135–163, 1997. ISSN 1065-8483. Citado na página 5.

De Luca, C. J. Electromyography. In: Encyclopedia of Medical Devices and Instrumentation. 2nd. ed. [S.l.: s.n.], 2006. p. 98–109. ISBN 0471732877. Citado 2 vezes nas páginas 6 e 7.

GALVANI, L. De viribus electricitatis in motu musculari commentarius. In: Bononiae: Ex Typographia Instituti Scientiarium. [S.l.: s.n.], 1791. Citado na página 5.

HERMENS, H. J. et al. Development of recommendations for SEMG sensors and sensor placement procedures. Journal of Electromyography and Kinesiology, v. 10, n. 5, p. 361–374, 2000. ISSN 10506411. Citado na página 11.

LI, G.; SCHULTZ, A. E.; KUIKEN, T. A. Quantifying pattern recognition- based myoelectric control of multifunctional transradial prostheses. IEEE Transactions on Neural Systems and Rehabilitation Engineering, v. 18, n. 2, p. 185–192, 2010. ISSN 15344320. Citado na página 5.

Motion Lab Systems Inc. EMG Analysis: A software user guide for EMG Graphing and EMG Analysis. 2009. Citado na página 9.

SILVA, I. A. R. da. Aquisição de sinais de miografia através de circuitos de baixo custo. In: UNIVERSIDADE FEDERAL DE SERGIPE. 27º Encontro de Iniciação Científica. [S.l.]: COPES - UFS, 2017. p. 320. Citado na página 6.

SparkFun Electronics. MyoWare Muscle Sensor. 2018. Disponível em: <https://www.sparkfun.com/products/13723>. (https://www.sparkfun.com/products/13723) Citado na página 6.

SUPUK, T. G.; SKELIN, A. K.; CIC, M. Design, development and testing of a low-cost sEMG system and its use in recording muscle activity in human gait. Sensors, v. 14, n. 5, p. 8235–8258, 2014. ISSN 1424-8220. Citado na página 6.

Texas Instruments Incorporated. Tiva™TM4C123GHCPM Microcontroller Datasheet. 2014. SPMS376E. Citado na página 8.

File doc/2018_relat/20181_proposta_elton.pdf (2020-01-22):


UNIVERSIDADE FEDERAL DE SERGIPE

CENTRO DE CIÊNCIAS EXATAS E TECNOLOGIA

DEPARTAMENTO DE COMPUTAÇÃO

Interface gráfica para digitalização de sinal miográfico

Proposta de Trabalho de Conclusão de Curso

Elton Moreira Carvalho

Departamento de Computação/UFS

São Cristóvão – Sergipe

UNIVERSIDADE FEDERAL DE SERGIPE

CENTRO DE CIÊNCIAS EXATAS E TECNOLOGIA

DEPARTAMENTO DE COMPUTAÇÃO

## Elton Moreira Carvalho

## Interface gráfica para digitalização de sinal miográfico

Proposta de Trabalho de Conclusão de Curso submetido ao Departamento de Computação da Universidade Federal de Sergipe como requisito parcial para a obtenção do título de Bacharel em Ciência da Computação.

Orientador(a): Daniel Oliveira Dantas

São Cristóvão – Sergipe

2017

# Sumário

Anexos | 12

# Lista de ilustrações

# Lista de tabelas

5
1

# Introdução

Desde os primórdios o ser humano procura maneiras de suprir os mais diversificados problemas encontrados no seu cotidiano, partindo de coisas simples como a dificuldade de trocar o canal da televisão, até outras um pouco mais complexas como a substituição de membros do corpo humano perdidos ou nunca desenvolvidos naturalmente.

Utilizando uma técnica de monitoramento da atividade elétrica das células musculares denominada eletromiografia é possível o desenvolvimento de próteses artificiais que simulam um membro do corpo humano, porém um conjunto de hardware e software capaz de captar e visualizar este tipo de sinal ainda é muito caro e de difícil acesso para a comunidade acadêmica, pensando nisso este plano de trabalho tem o objeto de desenvolver uma interface de software opensource capaz de exibir e armazenar sinais mioéletricos captados por um hardware externo desenvolvido pelo Departamento de Computação da Universidade Federal de Sergipe.

6
2

# Objetivos do projeto

Este plano de trabalho tem como objetivo criar um software, especificamente uma interface gráfica e firmware que permita um computador se comunicar com a placa TIVA EK-TM4C123GXL que irá receber, exibir e armazenar os sinais eletromiográficos capturados por um circuito externo desenvolvido no Departamento de Computação (DComp) da Universidade Federal de Sergipe (UFS), tornando assim fácil a utilização e tratamento destes sinais por outros pesquisadores.

A placa TIVA possui 12 conversores A/D, portanto, pode capturar 12 sinais a cada leitura. Será conectada a placas feitas sob medida, para capturar os sinais miográficos. Cada placa poderá possuir até 12 canais e os sinais podem ser multiplexados caso haja necessidade. A interface gráfica permitirá a escolha de parâmetros de captura e de exibição. Os parâmetros de captura devem ser transmitidos à placa TIVA por meio de um protocolo. Os parâmetros de exibição afetam apenas a visualização do sinal na tela do computador.

O software deve ser chamado através de um script bash que redireciona a saída para o arquivo especificado pelo primeiro parâmetro. O programa salvará a série temporal em um vetor na memória, pois no futuro pode ser necessário implementar outras funcionalidades mais flexíveis de visualização, exibição e edição do sinal. Para acelerar a alocação e a execução, o vetor deve crescer em blocos ao invés de uma posição por vez. O programa deve ter controle do número de posições usadas do vetor.

A interface gráfica não conhece a configuração do hardware, logo deve ser genérica de modo que funcione com qualquer configuração. O usuário, por sua vez, deve ser capaz de indicar a configuração correta do hardware, por exemplo, número de canais a serem lidos e número de placas a serem multiplexadas.

A placa TIVA recebe a solicitação e retorna uma informação de erro ou sucesso conforme sua capacidade. Futuramente pode-se definir um conjunto de funções para consultar a placa quanto a suas capacidades e configuração.

Capítulo 2. Objetivos do projeto | 7

Anexo a este documento possuí algumas imagens de como deverá ser a interface básica do software.

8
3

# Metodologia

## 3.1 Fases do Projeto

O projeto será dividido em três fases principais podendo existir sub-fases entre cada uma. A primeira fase é focada no estudo da plataforma TIVA e das funcionalidades do Python 2.7 para o desenvolvimento da interface gráfica e firmware, nesta fase será definida também as especificações do software. A segunda fase consiste no desenvolvimento do software em Python 2.7 referente à interface gráfica, seguindo as especificações da fase anterior. Por fim a terceira fase será destinada ao desenvolvimento da rede neural responsável por classificar os sinais obtidos pelo software.

## 3.2 Cronograma de Atividades

Meses
Atividade Out/17 Nov/17 Dez/17 Jan/18 Fev/18 Mar/18 Abr/18 Mai/18 Jun/18 Jun/18 Jul/18 Ago/18
01 | X | X
02 | X | X
03 | X | X
04 | | X | X | X | X
05 | | | | X | X | X | X
06 | | | | | | | | X
07 | | | | | | | | | X | X
08 | | | | | | | | | | X | X | X

Tabela 1 – Cronograma das atividades previstas

Capítulo 3. Metodologia | 9
| Legenda
01 | Estudar plataforma TIVA EK-TM4C123GXL
02 | Estudar o Code Composer Studio (CCS)
03 | Estudar documentação Python 2.7
04 | Desenvolver interface gráfica em Python 2.7
05 | Desenvolver código de integração com a TIVA
06 | Testar e validar os dados obtidos durante o processo
07 | Estudar Redes Neural
08 | Implementar e treinar a Rede Neural

Tabela 2 – Legenda do cronograma das atividades previstas

## 3.3 Recursos

Será necessário um hardware que realiza a captura dos sinais eletromiográficos, uma placa TIVA C Series TM4c123G para a conversão destes sinais e um ambiente Python 2.7 devidamente configurado para o desenvolvimento do software.

10
4

# Fontes de pesquisa

Para fins de estudo será utilizada a documentação fornecida pela Texas Instruments referente à placa EK-TM4C123GXL (INSTRUMENTS, 2017a) e ao ambiente de programação Code Composer Studio (INSTRUMENTS, 2017b). A documentação da linguagem de programação Python (PYTHON, 2017) e de suas bibliotecas QtPy4 (PYQT4, 2017), Serial (PYSERIAL, 2017) e PyQtGraph (PYQTGRAPH, 2017) servirá de base para o desenvolvimento do software de recepção e exibição dos sinais capturados.

A fundamentação teórica do trabalho será construída utilizando a base do Institute of Electrical and Electronics Engineers (IEEE, 2017) como principal fonte de pesquisa dos artigos e trabalhos relacionados ao tema aqui proposto.

11

# Referências

IEEE. IEEE Explore Digital Library. 2017. Disponível em: <http://ieeexplore.ieee.org.ez20.periodicos.capes.gov.br/Xplore/guesthome.jsp?reload=true>. (http://ieeexplore.ieee.org.ez20.periodicos.capes.gov.br/Xplore/guesthome.jsp?reload=true) Acesso em: nov 2017. Citado na página 10.

INSTRUMENTS, T. ARM® Cortex®-M4F Based MCU TM4C123G LaunchPad™ Evaluation Kit. 2017. Disponível em: <http://www.ti.com/tool/EK-TM4C123GXL>. Acesso em: nov 2017. Citado na página 10.

INSTRUMENTS, T. Code Composer Studio v7 Wiki. 2017. Disponível em: <http: //processors.wiki.ti.com/index.php/Category:Code_Composer_Studio_v7>. Acesso em: nov 2017. Citado na página 10.

PYQT4. PyQt4 Reference Guide¶. 2017. Disponível em: <http://pyqt.sourceforge.net/Docs/PyQt4/>. (http://pyqt.sourceforge.net/Docs/PyQt4/) Acesso em: nov 2017. Citado na página 10.

PYQTGRAPH. PyqtGraph Documentation. 2017. Disponível em: <http://www.pyqtgraph.org/documentation/>. (http://www.pyqtgraph.org/documentation/) Acesso em: nov 2017. Citado na página 10.

PYSERIAL. pySerial’s documentation. 2017. Disponível em: <https://pythonhosted.org/pyserial/>. (https://pythonhosted.org/pyserial/) Acesso em: nov 2017. Citado na página 10.

PYTHON. Python 2.7.14 documentation. 2017. Disponível em: <https://docs.python.org/2/>. Acesso em: nov 2017. Citado na página 10.

# Anexos


Referências | 13

Figura 1 – Tela Principal

Fonte: o autor

Figura 2 – Configuração de Exibição

Fonte: o autor

Referências | 14

Figura 3 – Configuração de Captura


Fonte: o autor

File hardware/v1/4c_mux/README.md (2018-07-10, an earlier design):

# DESIGN ESPECIFICATIONS FOR PROTEUS #

## 1. Clearences (apply to all layers) ##

* <b>Pad - Pad clearence:</b> 20th
* <b>Pad - Trace clearence:</b> 20th
* <b>Trace - Trace clearence:</b> 20th
* <b>Graphics clearence:</b> 10th
* <b>Edge/slot clearence:</b> 10th

## 2. Net Classes ##

### 2.1 Power ###

* <b>Routing styles</b>
  - Trace style: T20
  - Neck style: T20
  - Via style: default

### 2.1 Signal ###

* <b>Routing styles</b>
  - Trace style: T15
  - Neck style: T15
  - Via style: default
  
## 3. Defaults ##

* <b>Default styles</b>
  - Neck style: T10
  - Relief style: relief
  
* <b>Tolerances</b>
  - Curve tolerance: 10th
  - Rule check tolerance: 1um

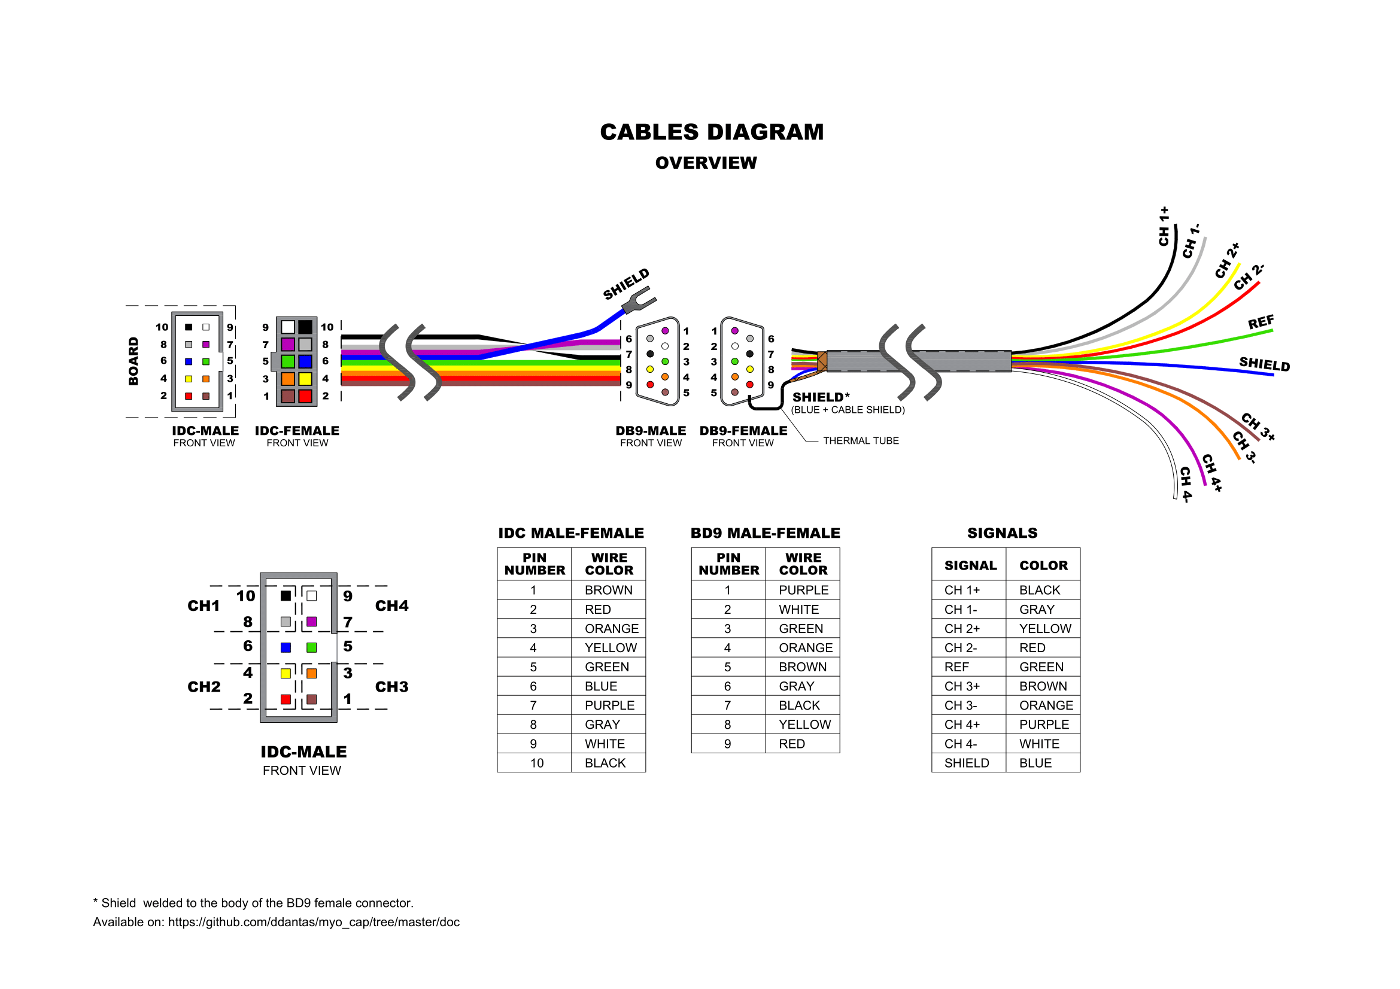
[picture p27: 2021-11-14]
doc/cables_diagram/Cables Diagram overview.png

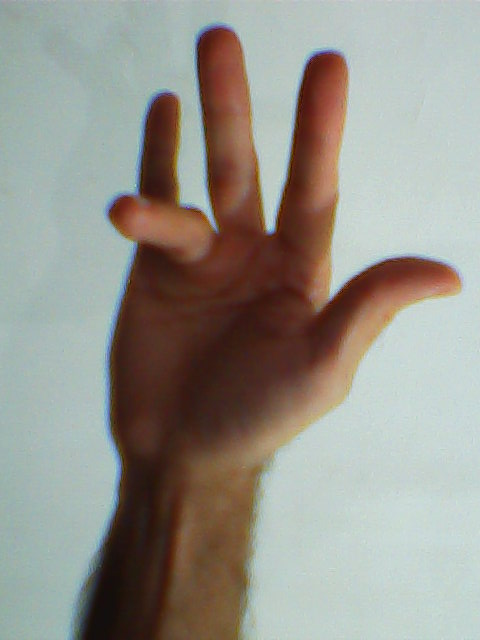
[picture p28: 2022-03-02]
software/interface/leap_cap/images/4an_flex.jpg

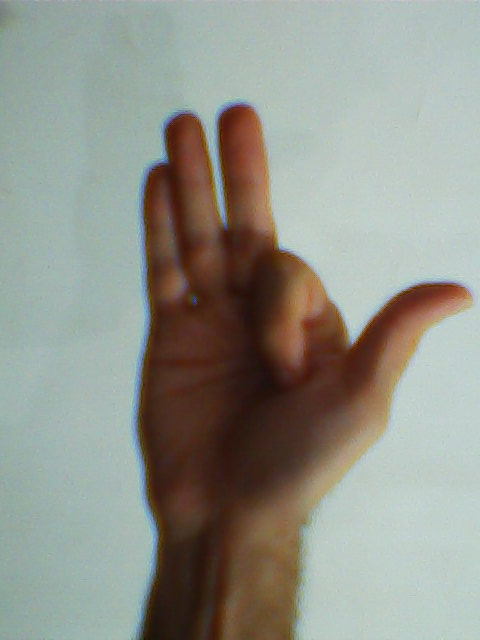
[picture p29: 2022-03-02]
software/interface/leap_cap/images/2in_flex_curl.jpg

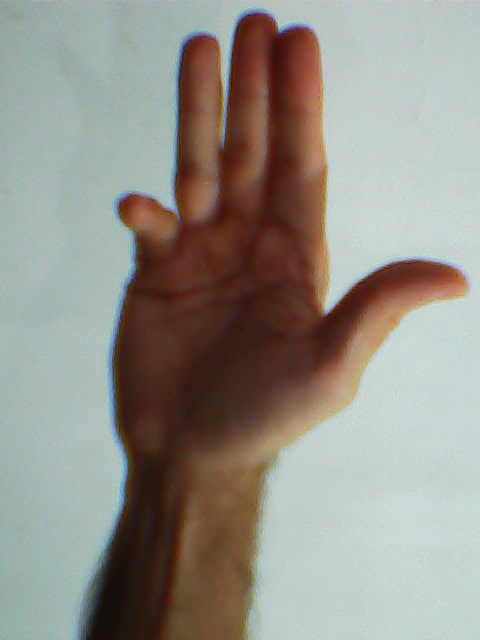
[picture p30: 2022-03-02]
software/interface/leap_cap/images/5mn_flex.jpg

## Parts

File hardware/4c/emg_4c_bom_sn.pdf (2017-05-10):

## BUILD OF MATERIALS (BOM)

CAPACITORS
Quantity | References | Value | Part Number
1 | C1 | 1.5 nF | C315C152J3G5TA7301 (https://www.digikey.com/product-detail/en/kemet/C315C152J3G5TA7301/C315C152J3G5TA7301-ND/6661428)
4 | C2, C6, C9, C12 | 10 µF | UKL1C100KDDANA (https://www.digikey.com/product-detail/en/nichicon/UKL1C100KDDANA/493-13395-ND/2598377)
4 | C3, C5, C8, C11 | 0.22 µF | UKL1HR22KDDANA (https://www.digikey.com/product-detail/en/nichicon/UKL1HR22KDDANA/493-15392-ND/2598486)

RESISTORS
Quantity | References | Value | Part Number
4 | R1, R16, R31, R46 | 15 kΩ | CF14JT15K0 (https://www.digikey.com/product-detail/en/stackpole-electronics-inc/CF14JT15K0/CF14JT15K0TR-ND/1741298)
8 | R2, R3, R17, R18, R32, R33, R47, R48 | 47 kΩ | CF14JT47K0 (https://www.digikey.com/product-detail/en/stackpole-electronics-inc/CF14JT47K0/CF14JT47K0TR-ND/1741444)
24 | R4, R5, R6, R7, R8, R9, R19, R20, R21, R22, R23, R26, R34, R35, R36, R37, R38, R41, R49, R50, R51, R52, R53, R56 | 10 kΩ | CF14JT10K0 (https://www.digikey.com/product-detail/en/stackpole-electronics-inc/CF14JT10K0/CF14JT10K0TR-ND/1741265)
2 | R10, R11 | 1 MΩ | CF14JT1M00 (https://www.digikey.com/product-detail/en/stackpole-electronics-inc/CF14JT1M00/CF14JT1M00TR-ND/1741316)
4 | R12, R27, R42, R57 | 1 kΩ | CF14JT1K00 (https://www.digikey.com/product-detail/en/stackpole-electronics-inc/CF14JT1K00/CF14JT1K00TR-ND/1741314)
8 | R13, R14, R28, R29, R43, R44, R58, R59 | 56 kΩ | CF14JT56K0 (https://www.digikey.com/product-detail/en/stackpole-electronics-inc/CF14JT56K0/CF14JT56K0TR-ND/1741469)
4 | R15, R30, R45, R60 | 1.5 kΩ | CF14JT1K50 (https://www.digikey.com/product-detail/en/stackpole-electronics-inc/CF14JT1K50/CF14JT1K50TR-ND/1741246)

INTEGRATED CIRCUITS
Quantity | References | Value | Part Number
6 | U1,U2,U3,U4,U5,U6 | TL084 | TL084CN (https://www.digikey.com/product-detail/en/texas-instruments/TL084CN/296-1784-5-ND/277429)

MISCELLANEOUS
Quantity | References | Value | Part Number
1 | ALIMENTACAO | SIL-100-03 | PPPC031LFBN-RC (https://www.digikey.com/product-detail/en/sullins-connector-solutions/PPPC031LFBN-RC/S7036-ND/810175)
1 | ELETRODOS | CONN- D9F | 5747840-6 (https://www.digikey.com/product-detail/en/te-connectivity-amp-connectors/5747840-6/A32094-ND/808649)
1 | OUTPUT - TIVA | CONN-H6 | PPTC061LFBN-RC (https://www.digikey.com/product-detail/en/sullins-connector-solutions/PPTC061LFBN-RC/S7004-ND/810145)

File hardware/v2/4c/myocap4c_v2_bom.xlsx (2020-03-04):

Designator | Manufacturer Part Number or Seeed SKU | Qty | Link
ELECTRODES | SBH11-PBPC-D05-RA-BK | 1 | https://www.digikey.ca/product-detail/en/sullins-connector-solutions/SBH11-PBPC-D05-RA-BK/S9177-ND/1990070
BUS | PRT-09280 | 1 | https://www.mouser.com/ProductDetail/SparkFun/PRT-09280
OUT | 68016-403HLF | 1 | https://www.digikey.co.il/product-detail/en/amphenol-icc-fci/68016-403HLF/609-6345-ND/4273587
MUX | CD4051BE | 1 | https://www.digikey.co.il/product-detail/en/texas-instruments/CD4051BE/296-2057-5-ND/67305
INAMP0, INAMP1, INAMP2, INAMP3 | AD620ANZ | 4 | https://www.digikey.co.il/product-detail/en/analog-devices-inc/AD620ANZ/AD620ANZ-ND/750967
AMPOPS | TL084CN | 1 | https://www.digikey.co.il/product-detail/en/texas-instruments/TL084CN/296-1784-5-ND/277429
REG | LM317AT/NOPB | 1 | https://www.digikey.co.il/product-detail/en/texas-instruments/LM317AT-NOPB/LM317AT-NOPB-ND/149025
D1, D2 | 1N4007 | 2 | https://www.digikey.ca/product-detail/en/on-semiconductor/1N4007/1N4007FSCT-ND/965481
D3 | BZX79C5V1 | 1 | https://www.digikey.com/product-detail/en/on-semiconductor/BZX79C5V1/BZX79C5V1-ND/977929
C1, C2, C3, C4 | UKL1C100KDD1TD | 4 | https://www.digikey.ca/product-detail/en/nichicon/UKL1C100KDD1TD/493-14344-3-ND/5699100
R1, R2, R3, R4, R9, R10, R11 | CF14JT4K70 | 7 | https://www.digikey.ca/product-detail/en/stackpole-electronics-inc/CF14JT4K70/CF14JT4K70TR-ND/1741428
R6, R7 | CF14JT10K0 | 2 | https://www.digikey.ca/product-detail/en/stackpole-electronics-inc/CF14JT10K0/CF14JT10K0TR-ND/1741265
R8 | CF14JT33K0 | 1 | https://www.digikey.ca/product-detail/en/stackpole-electronics-inc/CF14JT33K0/CF14JT33K0TR-ND/1741403
R12 | CF14JT100R | 1 | https://www.digikey.ca/product-detail/en/stackpole-electronics-inc/CF14JT100R/CF14JT100RTR-ND/1741261

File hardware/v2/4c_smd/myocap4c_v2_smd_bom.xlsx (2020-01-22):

Designator | Manufacturer Part Number or Seeed SKU | Qty | Link
ELECTRODES | SBH11-PBPC-D05-RA-BK | 1 | https://www.digikey.ca/product-detail/en/sullins-connector-solutions/SBH11-PBPC-D05-RA-BK/S9177-ND/1990070
BUS | PRT-09280 | 1 | https://www.mouser.com/ProductDetail/SparkFun/PRT-09280
OUT | 68016-403HLF | 1 | https://www.digikey.co.il/product-detail/en/amphenol-icc-fci/68016-403HLF/609-6345-ND/4273587
MUX | 74HC4051D,653 | 1 | https://www.digikey.ca/product-detail/en/nexperia-usa-inc/74HC4051D653/1727-2807-2-ND/763058
INAMP0, INAMP1, INAMP2, INAMP3 | AD620ARZ-REEL7 | 4 | https://www.digikey.ca/product-detail/en/analog-devices-inc/AD620ARZ-REEL7/AD620ARZ-REEL7TR-ND/617757
AMPOPS | TL084CDT | 1 | https://www.digikey.ca/product-detail/en/stmicroelectronics/TL084CDT/497-2217-2-ND/599258
REG | LM317MDTRKG | 1 | https://www.digikey.ca/product-detail/en/on-semiconductor/LM317MDTRKG/LM317MDTRKGOSCT-ND/917942
D1, D2 | S1B | 2 | https://www.digikey.com/product-detail/en/on-semiconductor/S1B/S1BFSCT-ND/965719
D3 | MM3Z3V3B | 1 | https://www.digikey.ca/product-detail/en/on-semiconductor/MM3Z3V3B/MM3Z3V3BCT-ND/1626881
C1, C2, C3, C4 | EEE-1CA100SR | 4 | https://www.digikey.ca/product-detail/en/panasonic-electronic-components/EEE-1CA100SR/PCE3878TR-ND/766045
R1, R2, R3, R4, R9, R10, R11 | ERA-3AEB472V | 7 | https://www.digikey.ca/product-detail/en/panasonic-electronic-components/ERA-3AEB472V/P4.7KDBTR-ND/1465870
R6, R7 | RNCP0603FTD10K0 | 2 | https://www.digikey.ca/product-detail/en/stackpole-electronics-inc/RNCP0603FTD10K0/RNCP0603FTD10K0TR-ND/2240139
R8 | ERA-3AEB333V | 1 | https://www.digikey.ca/product-detail/en/panasonic-electronic-components/ERA-3AEB333V/P33KDBTR-ND/1465890
R12 | RNCF0603DTE100R | 1 | https://www.digikey.ca/product-detail/en/stackpole-electronics-inc/RNCF0603DTE100R/RNCF0603DTE100RTR-ND/6263869

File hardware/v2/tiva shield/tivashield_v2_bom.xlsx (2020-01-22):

Designator | Manufacturer Part Number or Seeed SKU | Qty | Link
BUS | PPTC061LFBN-RC | 1 | https://www.digikey.com/product-detail/en/sullins-connector-solutions/PPTC061LFBN-RC/S7004-ND/810145
ANALOG_IN | 68002-404HLF | 1 | https://www.digikey.co.il/product-detail/en/amphenol-icc-fci/68002-404HLF/609-3305-ND/1878460
J1_J3, J4_J2 | 67996-420HLF | 2 | https://www.digikey.co.il/product-detail/en/amphenol-icc-fci/67996-420HLF/609-3221-ND/1878553
REG | LM7805CT/NOPB | 1 | https://www.digikey.com/product-detail/en/texas-instruments/LM7805CT-NOPB/296-47192-ND/3901929
POWER | 22-04-1031 | 1 | https://www.digikey.com/products/en?mpart=22-04-1031&v=23
USB_POWER | 22-04-1032 | 1 | https://www.digikey.com/products/en?mpart=22-04-1031&v=24
R1, R2, R3 | CF14JT1K00 | 3 | https://www.digikey.ca/product-detail/en/stackpole-electronics-inc/CF14JT1K00/CF14JT1K00TR-ND/1741314

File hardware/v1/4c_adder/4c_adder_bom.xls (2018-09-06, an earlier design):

BILL OF MATERIALS (BOM)
RESISTORS
Quantity | References | Value | Part Number
8 | R1, R2, R4, R5, R7, R8, R10, R11 | RES 10 kΩ | CF14JT10K0 (https://www.digikey.com/product-detail/en/stackpole-electronics-inc/CF14JT10K0/CF14JT10K0TR-ND/1741265)
4 | R3, R6, R9, R12 | RES 56 kΩ | CF14JT56K0 (https://www.digikey.com/product-detail/en/stackpole-electronics-inc/CF14JT56K0/CF14JT56K0TR-ND/1741469)
INTEGRATED CIRCUITS
Quantity | References | Value | Part Number
1 | U1 | CI TL084 | TL084CN (https://www.digikey.com/product-detail/en/texas-instruments/TL084CN/296-1784-5-ND/277429)
MISCELLANEOUS
Quantity | References | Value | Part Number
2 | INPUT, TO_TIVA | KK 254 5POS | 22032051
1 | POWER | KK 254 3POS | 22032031

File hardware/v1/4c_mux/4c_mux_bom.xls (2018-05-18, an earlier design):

BILL OF MATERIALS (BOM)
RESISTORS
Quantity | References | Value | Part Number
3 | R1, R2, R3 | 1,5 kΩ | CF14JT1K50 (https://www.digikey.com/product-detail/en/stackpole-electronics-inc/CF14JT1K50/CF14JT1K50TR-ND/1741246)
INTEGRATED CIRCUITS
Quantity | References | Value | Part Number
4 | U1,U2,U3,U4 | CD4051B | CD4051BE (https://www.digikey.com/product-detail/en/texas-instruments/CD4051BE/296-2057-5-ND/67305)
MISCELLANEOUS
Quantity | References | Value | Part Number
6 | BOARD_1-BOARD_4,OUTPUT,SELECT | SIL-100-05 | 22232051 (https://www.digikey.com/product-detail/en/molex-llc/0022232051/WM4203-ND/26673)
1 | POWER | SIL-100-03 | 22232031 (https://www.digikey.com/product-detail/en/molex-llc/0022232031/WM4201-ND/26669)

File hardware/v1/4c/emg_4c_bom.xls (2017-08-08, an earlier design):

BILL OF MATERIALS (BOM)
CAPACITORS
Quantity | References | Value | Part Number
1 | C1 | 1.5 nF | C315C152J3G5TA7301 (https://www.digikey.com/product-detail/en/kemet/C315C152J3G5TA7301/C315C152J3G5TA7301-ND/6661428)
4 | C2, C4, C6, C8 | 10 µF | UKL1C100KDDANA (https://www.digikey.com/product-detail/en/nichicon/UKL1C100KDDANA/493-13395-ND/2598377)
4 | C3, C5, C7, C9 | 0.22 µF | UKL1HR22KDDANA (https://www.digikey.com/products/en/capacitors/aluminum-electrolytic-capacitors/58?k=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)
RESISTORS
Quantity | References | Value | Part Number
8 | R1, R3, R16, R18, R29, R31, R42, R44 | 47 kΩ | CF14JT47K0 (https://www.digikey.com/product-detail/en/stackpole-electronics-inc/CF14JT47K0/CF14JT47K0TR-ND/1741444)
4 | R2, R17, R30, R43 | 15 kΩ | CF14JT15K0 (https://www.digikey.com/product-detail/en/stackpole-electronics-inc/CF14JT15K0/CF14JT15K0TR-ND/1741298)
24 | R4-R9, R19-R24, R32-R37, R45-R50 | 10 kΩ | CF14JT10K0 (https://www.digikey.com/product-detail/en/stackpole-electronics-inc/CF14JT10K0/CF14JT10K0TR-ND/1741265)
2 | R10, R11 | 1 MΩ | CF14JT1M00 (https://www.digikey.com/product-detail/en/stackpole-electronics-inc/CF14JT1M00/CF14JT1M00TR-ND/1741316)
4 | R12, R26, R38, R52 | 1 kΩ | CF14JT1K00 (https://www.digikey.com/product-detail/en/stackpole-electronics-inc/CF14JT1K00/CF14JT1K00TR-ND/1741314)
8 | R13, R14, R25, R27, R39, R40, R51, R53 | 56 kΩ | CF14JT56K0 (https://www.digikey.com/product-detail/en/stackpole-electronics-inc/CF14JT56K0/CF14JT56K0TR-ND/1741469)
4 | R15, R28, R41, R54 | 1.5 kΩ | CF14JT1K50 (https://www.digikey.com/product-detail/en/stackpole-electronics-inc/CF14JT1K50/CF14JT1K50TR-ND/1741246)
INTEGRATED CIRCUITS
Quantity | References | Value | Part Number
6 | U1,U2,U3,U4,U5,U6 | TL084CN | TL084CN (https://www.digikey.com/product-detail/en/texas-instruments/TL084CN/296-1784-5-ND/277429)
MISCELLANEOUS
Quantity | References | Value | Part Number
1 | ELETRODES | DB9-CONNECTOR | 5747840-6 (https://www.digikey.com/product-detail/en/te-connectivity-amp-connectors/5747840-6/A32094-ND/808649)
1 | JUMPER | SIL-100-02 | XG8T-0231 (https://www.digikey.com/products/en?keywords=XG8T-023)
1 | OUTPUT_TO_MUX | ARDUINO-SIL6 | PPTC061LFBN-RC (https://www.digikey.com/products/en?keywords=PPTC061LFBN-RC%20)
1 | POWER | TBLOCK-I3 | 1755749 (https://www.digikey.com/products/en?keywords=1755749)

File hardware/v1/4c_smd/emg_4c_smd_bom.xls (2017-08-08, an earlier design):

BILL OF MATERIALS (BOM)
CAPACITORS
Quantity | References | Value | Part Number
1 | C1 | 1.5 nF | ECH-U1H152GB5 (https://www.digikey.com/products/en?keywords=%20PCF1103CT-ND)
4 | C2, C4, C6, C8 | 10 µF | T491T106K016AT (https://www.digikey.com/product-detail/en/kemet/T491T106K016AT/399-8400-2-ND/2336362)
4 | C3, C5, C7, C9 | 0.22 µF | T499A224K035ATE18K (https://www.digikey.com/products/en?keywords=399-5068-2-ND)
RESISTORS
Quantity | References | Value | Part Number
4 | R1, R3, R16, R18, R29, R31, R42, R44 | 47 kΩ | 311-47.0KCRTR-ND (https://www.digikey.com/product-detail/en/yageo/RC0805FR-0747KL/311-47.0KCRTR-ND/727973)
8 | R2, R17, R30, R43 | 15 kΩ | RMCF0805JT15K0TR-ND (https://www.digikey.com/product-detail/en/stackpole-electronics-inc/RMCF0805JT15K0/RMCF0805JT15K0TR-ND/1757809)
24 | R4-R9, R19-R24, R32-R37, R45-R50 | 10 kΩ | 311-10.0KCRCT-ND (https://www.digikey.com/product-detail/en/yageo/RC0805FR-0710KL/311-10.0KCRCT-ND/730482)
2 | R10, R11 | 1 MΩ | RT1206BRD071ML (https://www.digikey.com/products/en?keywords=RT1206BRD071ML-ND)
4 | R12, R26, R38, R52 | 1 kΩ | 311-1.00KCRCT-ND (https://www.digikey.com/product-detail/en/yageo/RC0805FR-071KL/311-1.00KCRCT-ND/730391)
8 | R13, R14, R25, R27, R39, R40, R51, R53 | 56 kΩ | 311-56.0KCRCT-ND (https://www.digikey.com/product-detail/en/yageo/RC0805FR-0756KL/311-56.0KCRCT-ND/730980)
4 | R15, R28, R41, R54 | 1.5 kΩ | 311-1.50KCRCT-ND (https://www.digikey.com/product-detail/en/yageo/RC0805FR-071K5L/311-1.50KCRCT-ND/730443)
INTEGRATED CIRCUITS
Quantity | References | Value | Part Number
6 | U1,U2,U3,U4,U5,U6 | ADTL084ARZ | ADTL084ARZ-REEL7 (https://www.digikey.com/product-detail/en/analog-devices-inc/ADTL084ARZ-REEL7/ADTL084ARZ-REEL7TR-ND/1556005)
MISCELLANEOUS
Quantity | References | Value | Part Number
1 | ELETRODES | DB9-CONNECTOR | 5747840-6 (https://www.digikey.com/product-detail/en/te-connectivity-amp-connectors/5747840-6/A32094-ND/808649)
1 | JUMPER | SIL-100-02 | XG8T-0231 (https://www.digikey.com/products/en?keywords=XG8T-023)
1 | OUTPUT_TO_MUX | ARDUINO-SIL6 | PPTC061LFBN-RC (https://www.digikey.com/products/en?keywords=PPTC061LFBN-RC%20)
1 | POWER | TBLOCK-I3 | 1755749 (https://www.digikey.com/products/en?keywords=1755749)

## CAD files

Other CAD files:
doc/cables_diagram/Projeto_Cables Diagram_2010.dwg
hand/v1/Costas.0007.ipt
hand/v1/Falange-Distal.0004.ipt
hand/v1/Falange-media.0007.ipt
hand/v1/Falange-media2.0001.ipt
hand/v1/Falange-media2.0004.ipt
hand/v1/Falange-proximal.0008.ipt
hand/v1/Mao-robotica-alpha-costas.0006.iam
hand/v1/Mao-robotica-alpha.0002.iam
hand/v1/Motor.0003.ipt
hand/v1/Palma.0001.ipt
hand/v1/Polia.0002.ipt
hand/v2/Costas.ipt
hand/v2/Falange-Distal.ipt
hand/v2/Falange-media.ipt
hand/v2/Falange-media2.ipt
hand/v2/Falange-proximal.ipt
hand/v2/Mao-robotica-alpha-costas.iam
hand/v2/Mao-robotica-alpha.iam
hand/v2/Motor.ipt
hand/v2/Palma.ipt
hand/v2/Polia.ipt
hand/v2/Polia2.ipt

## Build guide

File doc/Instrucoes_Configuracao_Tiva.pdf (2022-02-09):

Links com Instruções de Instalação e manuais

- Informações de instalação do CCS versão 10: https://software-dl.ti.com/ccs/esd/documents/ccsv10_linux_host_support.html
- Informações de instalação do CCS versão várias versões: https://software-dl.ti.com/ccs/esd/documents/ccs_linux_host_support.html
- Manual do CCS -> Instalação: https://software-dl.ti.com/ccs/esd/documents/users_guide/ccs_installation.html#install ation-process
- Manual da biblioteca TivaWare: https://www.ti.com/lit/ug/spmu298e/spmu298e.pdf?ts=1614353598148&ref_url=https %253A%252F%252Fwww.ti.com%252Ftool%252FSW-TM4C

Links para download

- CCS: arquivo referente a Linux single file installer for CCS IDE para Linux ou Windows single file installer for CCS IDE para Windows: https://www.ti.com/tool/CCSTUDIO-SAFETY#downloads
- Biblioteca TivaWare: baixar arquivo referente a TivaWare for TM4C Series: https://www.ti.com/tool/download/SW-TM4C#downloads
- Projeto do Firmware da Tiva: https://github.com/ddantas/myo_cap/tree/master/software/firmware/Project%20Folde r
- LM Flash Programmer (Windows): https://www.ti.com/tool/LMFLASHPROGRAMMER
- UniFlash (Windows| Mac OS| Linux): https://www.ti.com/tool/UNIFLASH

Instalação do CCS no Ubuntu 20.04 LTS

1. Extraia o arquivo zip, é recomendado ler o arquivo readme para mais detalhes.
2. Para atualizar o SO use a seguinte linha de comando no terminal: sudo apt update.
3. Para instalar as bibliotecas necessárias use a seguinte linha de comando no terminal: sudo apt install libc6: i386 libusb-0.1-4 libgconf-2-4 libncurses5 libpython2.7 libtinfo5.
4. Execute o instalador.

5. Rode o script de instalação de drivers na pasta de instalação. Abra o terminal no diretório <CCS_INSTALL_DIR>/ccs/install_scripts e execute a seguinte linha de comando no terminal: sudo ./install_drivers.sh.

Instalação do CCS no Windows

1. Extraia o arquivo zip, é recomendado ler o arquivo Readme para mais detalhes.
2. A instalação do CCS depende de outros pacotes de software. Para Windows, esses pacotes serão instalados automaticamente como parte da instalação.
3. Execute o instalador.

Configuração do CCS

1. O contrato de licença deve ser aceito para continuar.
2. Selecione a opção custom installation.
3. Selecione o modelo TM4C12x.
4. Selecione o Spectrum Digital Debug Probes and Boards.
5. Somente para Windows. Clique em Permitir acesso se o Windows Defender estiver habilitado para instalar o CCS corretamente.

Instalação da TivaWare

1. Extraia o arquivo com terminação .exe na pasta ti do diretório de instalação do CCS.

Importação e configuração do projeto do firmware disponível no Git

1. Abra o CCS.
2. No CCS clique em Project -> Import CCS projects.
3. Busque e selecione a pasta EMG2 (myo_cap/software/firmware/Project Folder/EMG2) no local em que o projeto foi extraído.
4. Clique em Finish.
5. No Project Explorer clique com o botão direito em EMG2. Em seguida, clique em Properties.

6. Na aba General selecione em Configuration selecione Debug [active]. Verifique se o microcontrolador selecionado é o da placa Tiva, se há um compilador válido selecionado e se Stellaris in-Circuit Debug Interface está selecionado em Connection.
7. Na aba Build do Project Explorer clique na aba Variables, clique em Edit e selecione a variável TIVAWARE_INSTALL.
8. Clique no botão Browser e aponte a pasta de extração da TivaWare (home/usuario/ti/ccs1040/SW-TM4C-2.2.0.295). Aplique e feche as configurações do projeto.
9. No Project Explorer clique com o botão direito em Clean Project. Em seguida clique em Build Project.

Configuração do LM Flash Programmer (Windows)

1. Extraia o arquivo e execute instalador.
2. É necessário abrir o programa como administrador.
3. Conecte a placa Tiva ao computador na entrada USB Connector for power & emulation da placa (entrada mais próxima ao switch).
4. Na aba Configuration em Quick Set selecione a opção TM4C123G LaunchPad.
5. Na aba Program em Select .bin file clique no botão Browser e aponte o arquivo EMG2.bin na pasta que está o projeto disponível no Git (myo_cap/software/firmware/Bin File/EMG2.bin).
6. Em Erase Method selecione a opção Erase Entire Flash - (faster).
7. Marque a opção Verify After Program.
8. Marque a opção Reset MCU After Program.
9. Clique em Program.

Configuração da placa Tiva utilizando o CCS

1. Conecte a placa Tiva ao computador na entrada USB Connector for power & emulation da placa.
2. Abra o CCS.

3. Clique em CCS Debug (geralmente fica no canto superior direito).
4. Clique em Build ‘Debug’ for project ‘EMG2’ (martelo).
5. Clique em Debug EMG2 (besouro).

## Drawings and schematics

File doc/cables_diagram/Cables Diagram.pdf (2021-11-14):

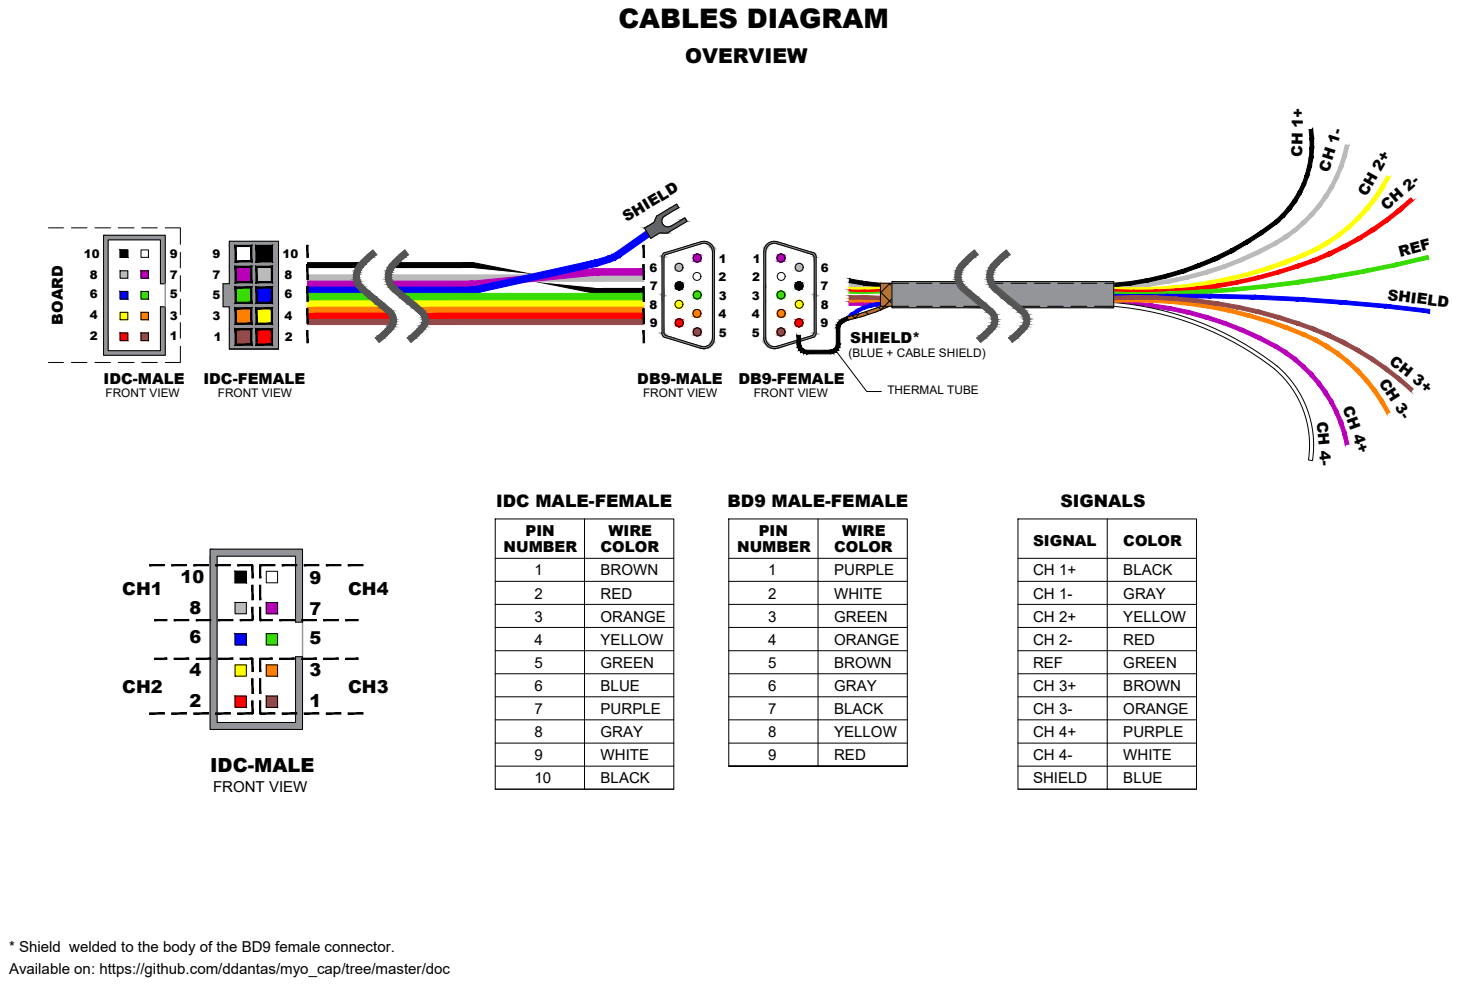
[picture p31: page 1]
REF; SHIELD

BOARD FRONT VIEW FRONT VIEW FRONT VIEW 7 8 5 6 3 4 1 2 9 10 54321 9876 Available on: https://github.com/ddantas/myo_cap/tree/master/doc CABLES DIAGRAM CH 1+ CH 1- CH 2+ CH 2- REF BLACK GRAY YELLOW RED GREEN CH 3+ CH 3- CH 4+ CH 4- SHIELD BROWN ORANGE PURPLE WHITE BLUE 8 7 6 5 4 3 2 1 10 9 IDC-MALE FRONT VIEW CH3 CH4 CH2 CH1 SIGNAL COLOR * Shield welded to the body of the BD9 female connector. 12345 BROWN RED ORANGE YELLOW GREEN 678910 BLUE PURPLE GRAY WHITE BLACK COLOR PIN NUMBER WIRE IDC MALE-FEMALE 12345 PURPLE WHITE GREEN ORANGE BROWN 6789 GRAY BLACK YELLOW RED COLOR PIN NUMBER WIRE BD9 MALE-FEMALE SIGNALS THERMAL TUBE

CH 4- OVERVIEW DB9-MALE54321 9876 8 7 6 5 4 3 2 1 10 9 IDC-MALE IDC-FEMALE SHIELD FRONT VIEW

DB9-FEMALE SHIELD* (BLUE + CABLE SHIELD)

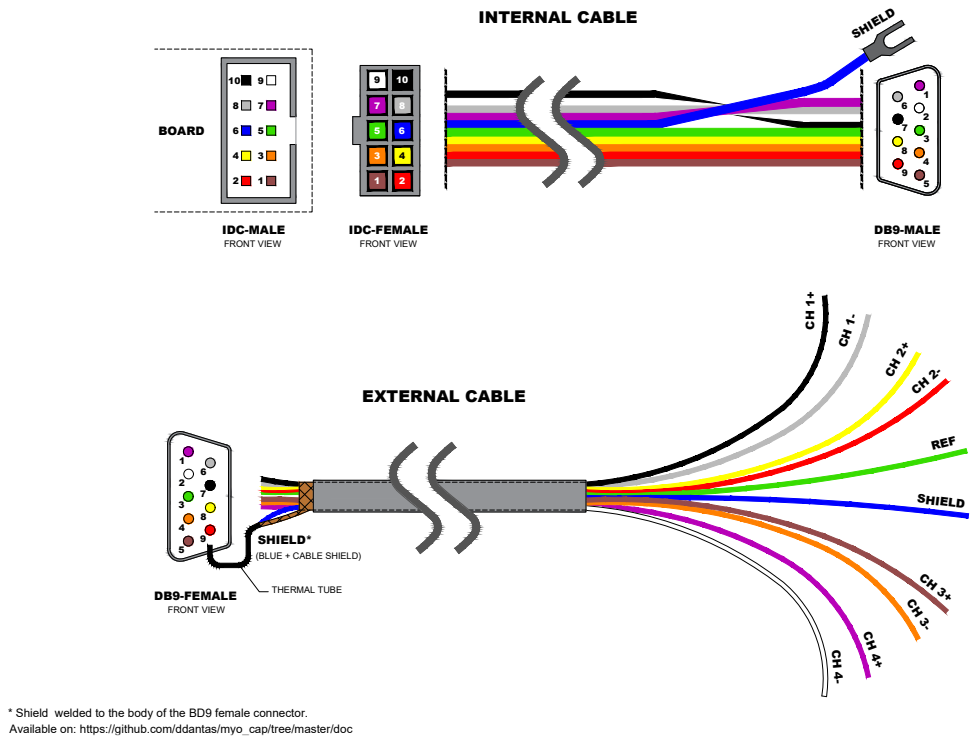
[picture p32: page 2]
DB9-MALE⁵⁴³²¹ ⁹⁸⁷⁶ 54321; 9 DB9-FEMALEIDC-MALE; IDC-FEMALE; SHIELD FRONT VIEW; FRONT VIEW; FRONT VIEW FRONT VIEW BOARD; SHIELD* (BLUE + CABLE SHIELD); REF; SHIELD

CH 4- INTERNAL CABLE EXTERNAL CABLE Available on: https://github.com/ddantas/myo_cap/tree/master/doc * Shield welded to the body of the BD9 female connector. THERMAL TUBE

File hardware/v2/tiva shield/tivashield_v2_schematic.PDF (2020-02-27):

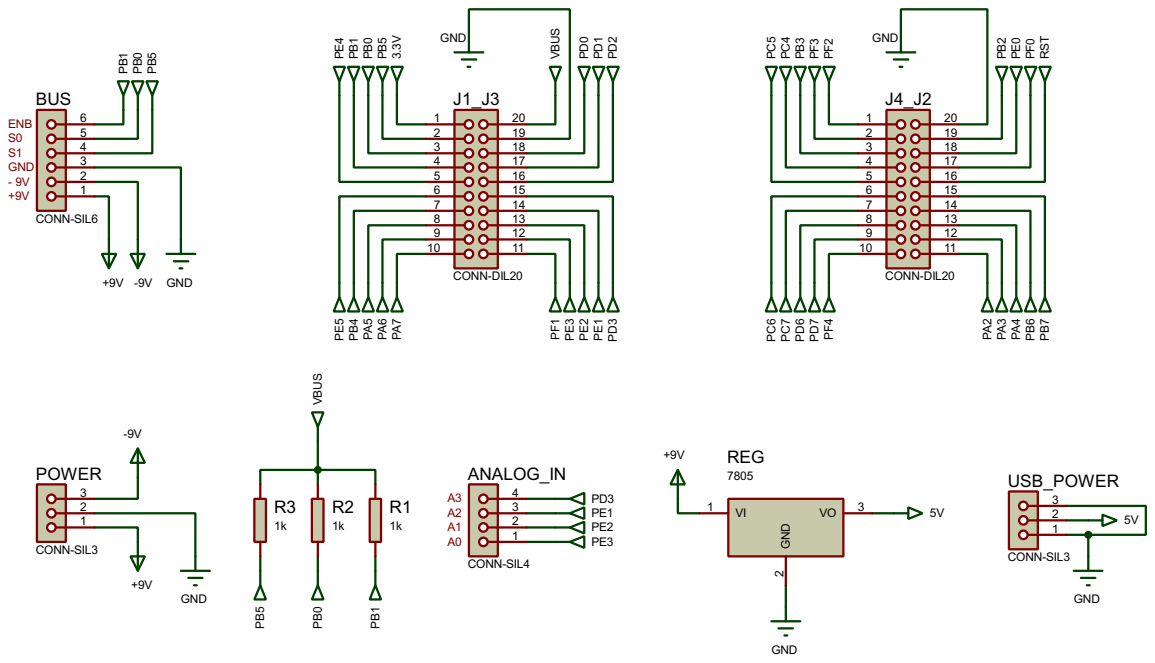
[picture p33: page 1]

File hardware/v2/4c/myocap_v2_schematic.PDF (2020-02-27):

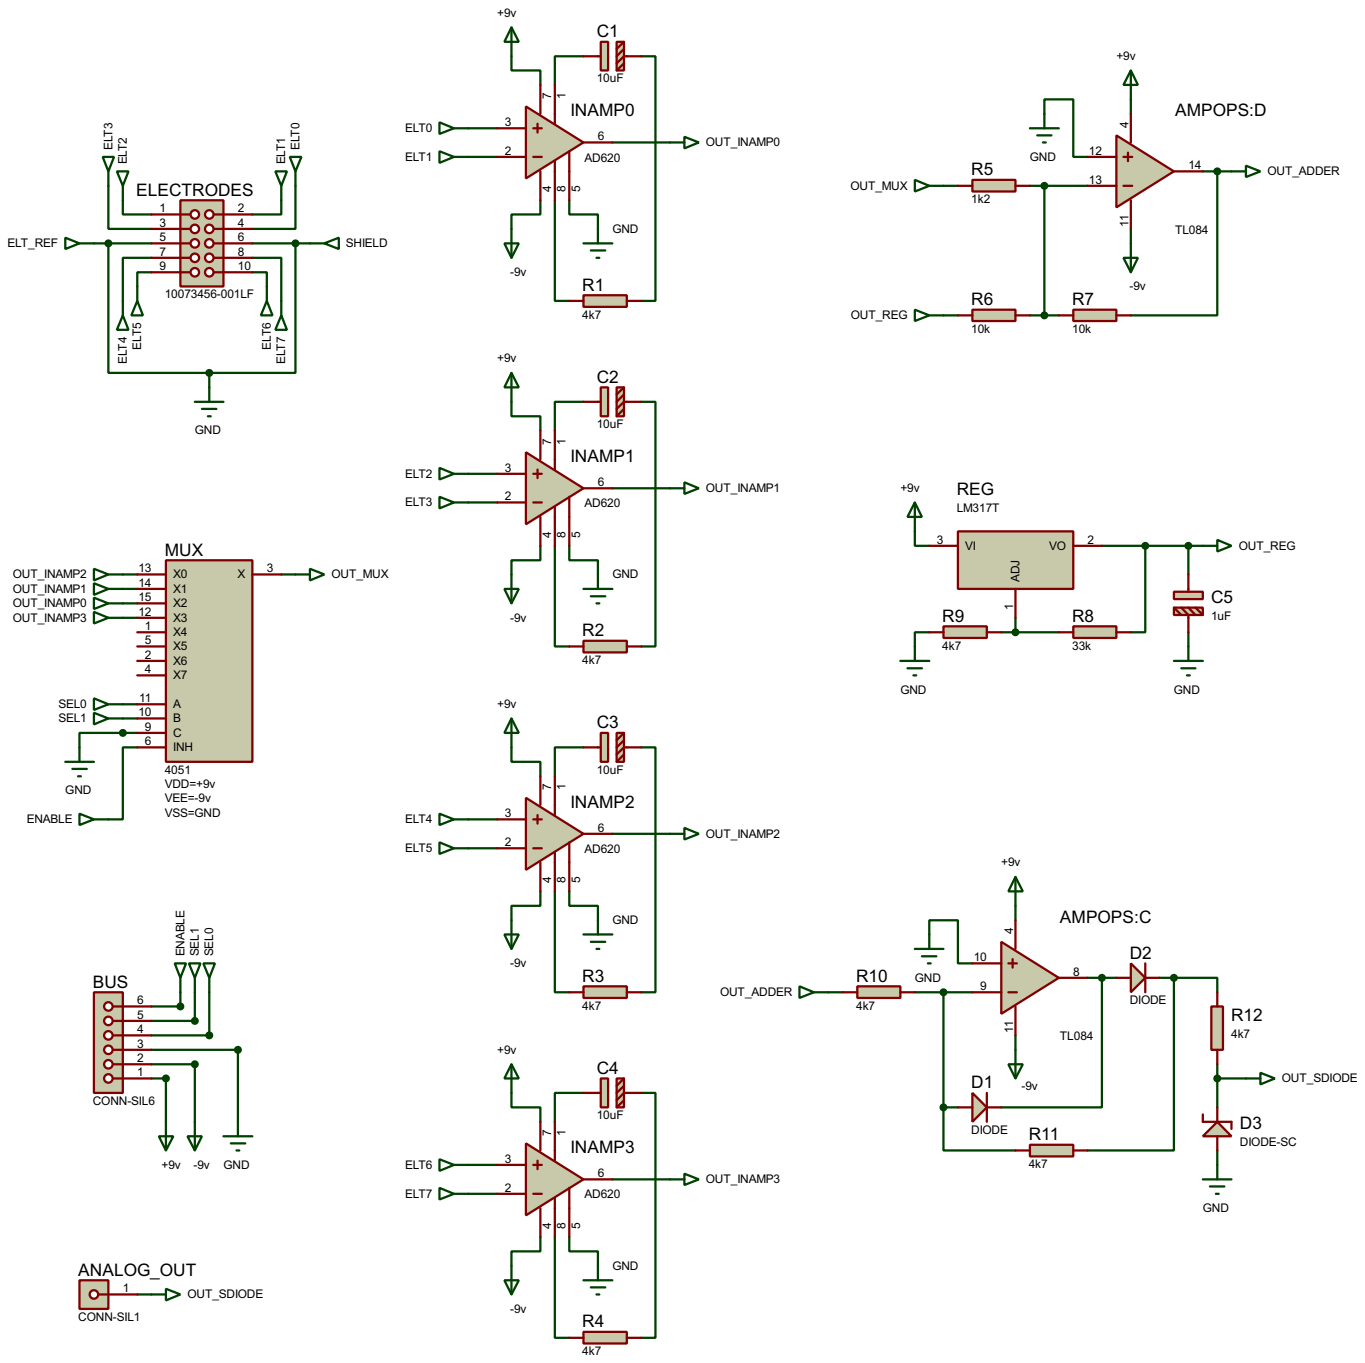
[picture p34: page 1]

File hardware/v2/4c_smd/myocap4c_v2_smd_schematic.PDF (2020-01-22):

C1

R5

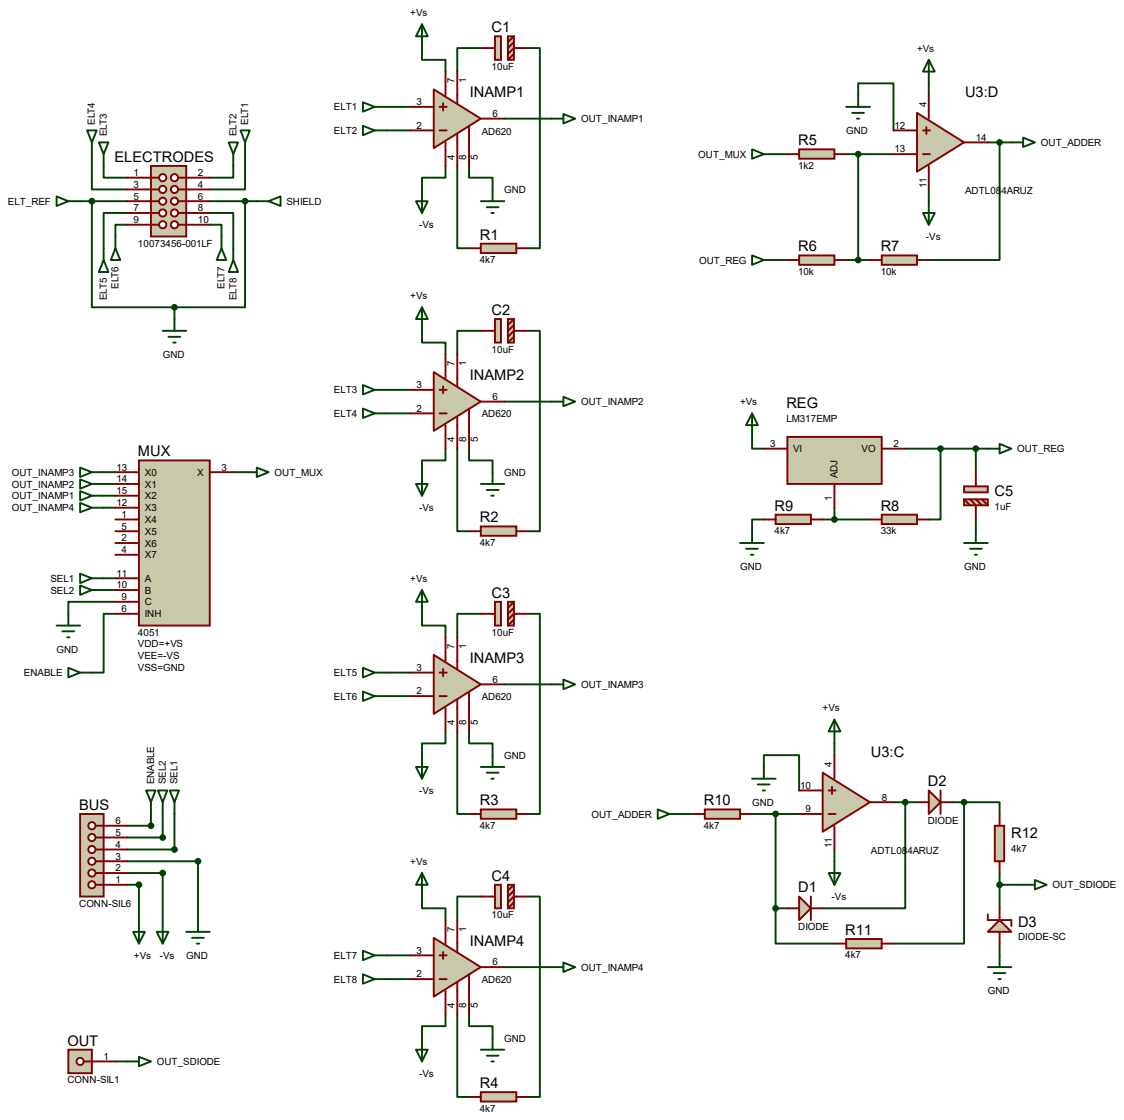
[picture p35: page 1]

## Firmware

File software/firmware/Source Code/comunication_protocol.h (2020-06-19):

#include <stdint.h>
#include <string.h>
#include "tiva_HAL.h"

//// Structs ///////////////////////////////////////////////////////////////////////////////////////////////////////////////////////////////////////////


// Defines a structure type with a uint32_t parameter to be used by the communication packet.

typedef struct {

    //Little-Endian Storage Structure

    uint16_t command       ;     // Byte[0-1] ; Size = 2 bytes ; Byte Offset = 0
    // Padding             ;     // Byte[2-3] ; Size = 2 bytes ; Byte Offset = 2                 // 2 Bytes added after "command" for the address of "uint32_operand" be a multiple of 4(bytes).
    uint32_t uint32_operand;     // Byte[4-7] ; Size = 4 bytes ; Byte Offset = 4

    //uint8_t  Chk_Sum_8bits 8;                                                                 // *One Byte is used for a CheckSum of the last 8 bits(Not yet implemented).

} uint32_parameter_packet;



// Defines a structure type with a float32 parameter to be used by the communication packet.


typedef struct {

    uint16_t command       ;      // Byte[0-1] ; Size = 2 bytes ; Byte Offset = 0
    // Padding             ;      // Byte[2-3] ; Size = 2 bytes ; Byte Offset = 2                // 2 Bytes added after "command" for the address of "float_operand" be a multiple of 4(bytes).
    float    float_operand ;      // Byte[4-7] ; Size = 4 bytes ; Byte Offset = 4

    //uint8_t Chk_Sum_8bits 8;                                                                   // *One Byte is used for a CheckSum of the last 8 bits(Not yet implemented).

} float_parameter_packet;




// Defines three perspectives for a packet: 1 - Packet with a uin32 operand; 2 - Packet with a float operand; 3 - uint32 vector.

typedef union{
        uint32_parameter_packet uint32_param_pkt;
        float_parameter_packet  float_param_pkt;
        uint8_t                 bytes[8];

} comunication_packet;





//// Constants ///////////////////////////////////////////////////////////////////////////////////////////////////////////////////////////////////////////

// Commands to be interpreted by the command handler
//
// ASCII Dictionary
//
// a = 0x61
// b = 0x62
// c = 0x63
// e = 0x65
// f = 0x66
// g = 0x67
// i = 0x69
// k = 0x6b
// m = 0x6d
// n = 0x6E
// o = 0x6f
// p = 0x70
// q = 0x71
// r = 0x72
// s = 0x73
// u = 0x75
// v = 0x76
// w = 0x77

#define START_TRANSMISSION          0x6169  //  "ai"
#define STOP_TRANSMISSION           0x6173  //  "as"

#define SET_TRANSMISSION_MODE       0x736d  //  "sm"
#define SET_SAMPLE_RATE             0x7372  //  "sr"
#define SET_NUMBER_CHANNELS         0x7363  //  "sc"
#define SET_NUMBER_BOARDS           0x7362  //  "sb"
#define SET_NUMBER_BYTES_IN_PACKET  0x7370  //  "sp"
#define SET_BITS_PER_SAMPLE         0x7373  //  "ss"
#define SET_ADC_ACQUISITION         0x6661  //  "fa"

#define GET_TRANSMISSION_MODE       0x676d  //  "gm"
#define GET_SAMPLE_RATE             0x6772  //  "gr"
#define GET_NUMBER_CHANNELS         0x6763  //  "gc"
#define GET_NUMBER_BOARDS           0x6762  //  "gb"
#define GET_NUMBER_BYTES_IN_PACKET  0x6770  //  "gp"
#define GET_BITS_PER_SAMPLE         0x6773  //  "gs"

#define ACK                         0x6f6b  //  "ok"
#define NAK                         0x6d65  //  "me"


// Return Types

#define INT32_VALUE                 0x7675  //  "vu"
#define FLOAT32_VALUE               0x7666  //  "vf"
#define STREAMING_PKT               0x6d73  //  "ms"
#define ERROR_MSG                   0x6d65  //  "me"
#define WARNING_MSG                 0X6d77  //  "mw"


// Function Generator Commands

#define SET_FUNC_GEN_FREQUENCY      0x7366  //  "sf"
#define SET_FUNC_GEN_SQUARE_WAVE    0x6671  //  "fq"
#define SET_FUNC_GEN_SAWTOOTH_WAVE  0x6677  //  "fw"
#define SET_FUNC_GEN_SIN_WAVE       0x666E  //  "fn"

#define GET_FUNC_GEN_WAVE_FORM      0x6777  //  "gw"
#define GET_FUNC_GEN_FREQUENCY      0x6766  //  "gf"



// Error Messages

// Out of Range

#define MSG_OOR_FUNC_GEN_FREQUENCY   " Hz it is Outside the Range Accepted by the Function Generator.\nTry a Value bigger than 0 and less than SampleRate / 2.\nFor the Current Configuration, Please use a value between: \0"
#define MSG_OOR_SAMPLE_RATE          " Hz of Sample Rate it is Outside the Range Accepted by the Board.\nTry a Value bigger than 0 and less or equal than 1MHZ / (Total Number of Channels).\nFor the Current Configuration, Please use a value between: \0"
#define MSG_OOR_NUMBER_CHANNELS      " Channel(s) it out of the Outside the Range Accepted by the Board.\nPlease use a value between: \0"
#define MSG_OOR_NUMBER_BOARDS        " Acquisition Board(s) it is Outside the Range Accepted by the Board.\nPlease use a value between: \0"
#define MSG_OOR_BYTES_IN_PACKET      " Byte(s) in a Packet it is Outside the Range Accepted by the Board.\nFor the current settings. Please use a value between: \0"
#define MSG_OOR_BITS_PER_SAMPLE      " bits per Sample it is Outside the Range Accepted by the Board.\nPlease use a value between: \0"

// Types of Acquisition

#define MSG_UKN_TYPE_OF_ACQUISIION   "The Board do not Recognize this Acquisition Mode."


// Types of Transmission Mode

#define MSG_UKN_TRANSMISSION_MODE    "The Board do not Recognize this Transmission Mode."


// Properties ofcomunication_packet: Offset and Size in Bytes.

#define OFFSET_COMMAND              0
#define OFFSET_OPERAND              4

#define SIZE_COMMAND                2
#define SIZE_OPERAND                4

//

#define LENGTH_BUFFER_IN           64
#define LENGTH_BUFFER_OUT          64



// functions prototypes

void command_handler (comunication_packet *pkt_received, tiva_status *tiva_actual_state );
void send_packet     (comunication_packet *pkt_to_send                                  );
void recieve_packet  (comunication_packet *pkt_to_be_received                           );
void stop_trasmission(                                                                  );

uint32_t msg_generator( uint32_t value, char* default_msg, uint32_t start_range, uint32_t end_range, char* out_msg );
// Macros

//# define MSG_OOR_BITS_PER_SAMPLE ()

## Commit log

2017-02-01 atualização do relatório para correção do valor de fc1
2017-02-01 Remoção de arquivo de teste placehold.txt
2017-02-01 upload do design de circuito para um canal no proteus
2017-02-02 upload arquivos impressão circuito 1 canal
2017-04-20 pasta para hardware de 1 canal
2017-04-20 pasta para hardware de 4 canais
2017-04-28 Correções no circuito de 4 canais
2017-04-28 Bill of materials
2017-05-11 Four-channel board oscilloscope capture
2017-06-18 added capture code / added jp code / updated software files
    [uartstdio.obj]
2017-06-21 upload 4 channel SMD PCB files
2017-06-28 Added 4 channel SMD PCB files
2017-06-29 Added 4 channel SMD PCB new files
2017-07-04 renamed: tiva/placeholder.txt -> energia/placeholder.txt new file: energia/sample4ch.ino renamed: myo_capture/myo_capture.py -> interface/myo_capture.py renamed: myo_capture/myo_capture_v2.py -> inte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
    [uartstdio.obj]
2017-07-07 renamed: 4c/emg_4c_bom_sn.pdf -> 4c/emg_4c_bom.pdf modified: ../software/energia/sample4ch.ino
2017-07-18 new file: doc/20171_relat/isac_20172_final.pdf deleted: hardware/4c_SMD/emg_4c_smd_bom.pdf new file: hardware/4c_SMD/emg_4c_smd_bom.xls modified: software/energia/sample4ch.ino
    [emg_4c_smd_bom.xls]
2017-07-18 new file: doc/20172_relat/isac_20172_final.docx renamed: doc/20171_relat/isac_20172_final.pdf -> doc/20172_relat/isac_20172_final.pdf renamed: hardware/4c_SMD/emg_4c_smd.pdsprj -> hardware/4c_smd/emg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
    [emg_4c_smd_bom.xls]
2017-07-21 modified: emg_4c_smd_bom.xls
    [emg_4c_smd_bom.xls]
2017-07-21 modified: emg_4c_smd_bom.xls new file: emg_4c_smd_gbr.zip deleted: emg_4c_smd - CADCAM.ZIP modified: ../../software/energia/sample4ch.ino modified: ../../software/interface/myo_capture.py modified: .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
    [emg_4c_smd_bom.xls]
2017-07-22 Added new files
    [emg_4c_smd_bom.xls]
2017-07-29 deleted: 4c/emg_4c_bom.pdf new file: 4c/emg_4c_bom.xls modified: 4c/emg_4c_gbr.zip modified: 4c/emg_4c_proteus.pdsprj modified: 4c_smd/emg_4c_smd_bom.xls renamed: 4c_smd/emg_4c_smd_grb.ZIP -> 4c_smd/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
    [emg_4c_bom.xls, emg_4c_smd_bom.xls]
2017-08-08 update bom 4c
    [emg_4c_bom.xls]
2017-09-12 feat: add tiva.py
    [uartstdio.obj]
2018-05-10 remove files
    [4c_add_bom.xls]
2019-04-19 creating folders per version
    [4c_adder_bom.xls, 4c_mux_bom.xls, emg_4c_bom.xls, emg_4c_smd_bom.xls]
2019-04-20 update of labels of myocap_v2 board
2019-05-10 update tivashield board
2019-05-23 update tiva shield board
2019-06-04 update myocap v2 boards
2019-06-21 creating Tiva Shield BOM
    [myocap4c_v2_bom.xlsx, tivashield_v2_bom.xlsx]
2019-06-21 creating MyoCap BOM
    [myocap4c_bom.xlsx]
2019-07-09 Added 4c_smd folder to hardware/v2.
    [myocap4c_v2_smd_bom.xlsx]
2019-08-07 Updated capture board v2 4c SMD.
2019-10-23 Added hand files.
    [Costas.0007.ipt, Costas.ipt, Falange-Distal.0004.ipt, Falange-Distal.ipt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]
2019-11-20 deleted: software/energia/placeholder.txt deleted: software/energia/sample4ch.ino modified: software/interface/.idea/workspace.xml modified: software/interface/config/settings deleted: software/inter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
2019-11-20 deleted: hardware/v2/4c/myocap4c_v2_gbr.ZIP deleted: hardware/v2/4c/myocap4c_v2_proteus.pdsprj deleted: hardware/v2/4c/myocap4c_v2_schematic.PDF modified: hardware/v2/tiva shield/tivashield_v2_bom.xl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
    [tivashield_v2_bom.xlsx]
2020-01-31 modified: interface/.idea/workspace.xml new file: interface/Board.py modified: interface/SerialPort.py modified: interface/Settings.py new file: interface/Tiva.py modified: interface/UiCaptureSetting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
2020-02-07 modified: software/interface/.idea/workspace.xml modified: software/interface/Board.py modified: software/interface/WinCaptureSettings.py modified: software/interface/WinDisplaySettings.py modified: 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
2020-03-04 update myocap v2 BOM
    [myocap4c_v2_bom.xlsx]
2020-05-01 add features: save capture to file and read capture from file
    [2020-04-30_23-20-07.csv, 2020-04-30_23-41-37.csv, 2020-04-30_23-42-57.csv, 2020-05-01_00-27-29.csv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]
2020-05-06 Bugs Fixed and Features Added.
    - Fixed bugs related to the flow control (Start , Stop and Show).
    - Buttons "Apply" send commands to the Board.
    - New Feature provides Synchronization betwen Interface and the Board used.
2020-06-03 add write function to Board.py
2020-06-06 remove old capture files
    [2020-04-30_23-20-07.csv, 2020-04-30_23-41-37.csv, 2020-04-30_23-42-57.csv, 2020-05-01_00-27-29.csv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]
2020-06-10 Feature: Packed Mode Transmission Working. Interface and Firmware: Bugs Fixed. Please Read the Description.
    Changes in Interface Code:
    - New Class respossible by Unpacking Samples Added (Unpacker).
    - New Command to change the Transmission Mode was created.
    - Checkbox "Transmission Mode" connected to the command that change the Transmission Mode.
    - Method "receive()" was changed to Support the new Transmission Mode.
    - Bug related to transmission parameters change was removed.
    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
2020-06-19 use settings.getSampleRate() at WinStresstest.py
    to determinate the expected samples during test;
    'Expected samples: ' now counts up;
    also fixed the display for 'Dropped samples:' .
2020-06-28 Bug Related to Sample Rate of the Mux Fixed!
    - Please Update the Firmware.
2020-07-01 Debug Feature now it's Optional.
    - The Debug through print comands is now selectable by the "DEBUG" value constant in the "Constant" File.
    - New File "Constants.py" added. The constants will be imported by it.
2020-10-23 New changes in the Myocap firmware code.
    New changes in the Myocap firmware code:
    - The selection pins used in the Tiva are compatible with the Myocap Shield now.
    - The pins of the Tiva ADC are being switched to acquire samples of multiples acquisition boards.
    - The pins used in the Tiva ADC are compatible with the Myocap Shield now.
    - An alternative set of pins for the Tiva ADC are preconfigured and available in tiva_HAL.h file.
    To use the alternative set of pins, uncomment the line of code "#define USE_ADC_ALTERNATIVE_PINS" in tiva_HAL.h file.
2021-01-31 LeapCap: Keys pressed in the subject window are geting captured by "WinMain".
    - "WinSubject" was fixed.
    - "WinMain" it's managing the opening and the closure of the subject window.
    - "WinMain" it's handling the subject window.
    - "WinMain" it's printing the keys pressed in the subject window.
2021-02-03 "TextFile" was checked and it's ready to be used in LeapCap log. Please see the description.
    - Just one line of code was impeding the code to work with LeapCap.
    - Two minnor things was changed.
    - Although the TextFile it's done, a method need to be writen to send the metadata and others informations before the samples data be sended.
2021-02-03 "WinSubject": Finger joints have a panel inside the subject window. Code was improoved.
    - A new method to print panels on the screen was created. It helps in the positioning of the graphical elements.
    - The time panel had your dimenssions corrected.
    - A panel that will contain the joint angles of the fingers was created and positioned.
2021-03-03 PyGameLibExt.py: Image class was built and tested. Please see the description.
    - Image class was developed and tested.
    - Draw method in PyGameLibExt.py now have support to draw Images objects.
    Notes: The current implementation of Image class do not keep the aspect ratio of the images. That will be done in the next iteration of this code.
    The documentation of the Image class will be done in the future.
2021-03-17 New Subject Window was improved. Please read the description.
    Current Progress:
    - Images are being loaded into images objects.
    - Images are being added into the Images Layout.
    - Images Layout are being added into Main Panel.
    - The Subject window already supports resizing.
    - The code in UISubject was refactored.
    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
2021-03-31 UiSubject code it's complete. Please see the description to know the main changes.
    - Small refactorization of the code.
    - The 'createLetters' method was widely extended:
    - For a correct display of the letters it was necessary to standardize the size of the letters.
    To do this, it is necessary to: 1- Know the largest dimensions between the letters. 2 - To generate background surfaces with these dimensions for each letter. 3 - Merge the surfaces of the letters wi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
    - 'createFingersLettersLayout' method was developed.
    - The Fingers Letters Layout was added to the Main Panel.
    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
2021-07-07 The routine file termination was updated to "csv".
    [default.csv]
2021-07-09 The gesture times of the routine file were updated. From seconds to miliseconds. As stated in the requirements document.
    [default.csv]
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2021-11-14 Cables Diagram was modded and moved to the doc folder. AutoCad files were included.
    [Projeto_Cables Diagram_2010.dwg]
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2022-03-02 Added routines and new images of gestures.
    [01_hand_close.csv, 02_hand_flex.csv, 03_hand_curl.csv, 11_fingers_close.csv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]
